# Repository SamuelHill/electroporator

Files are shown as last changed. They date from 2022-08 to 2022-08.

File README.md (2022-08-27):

# Electroporator PCB

Various PCB designs for a simple, versatile, and inexpensive electroporator. Inspiration and original design from [T. Bullman, et. al. 2015](https://onlinelibrary.wiley.com/doi/10.1111/dgd.12216). As stated in the paper:

> Electroporation is a useful technique to study gene function during development but its broad application is hampered due to the expensive equipment needed.

While I agree with this and the rest of the paper largely, I believe the design set forth is both cluttered and unnecessarily complicated. This is mainly due to the use of a breadboard (or PCB breadboard), and given the current capabilities and price point of manufacturing a custom PCB this seems the obvious place to start for simplification. To that end, I designed a simple PCB that also contains much of the needed information for construction and operation on the silkscreen. After successfully implementing and using the v.0 system, I also designed and am working on implementing a handful of v.1 boards.

The layout of this project is a series of nested KiCad projects for easy navigation within KiCad. To better show the functionality of the HE721A IC's - and add this product and footprint - I created a custom part (found in the parts folder). In the gerber folder is the compiled output of the v.0 board which has been printed, tested, and used successfully. As more of the designs are tested I will add more completed gerber files. The archive folder can be ignored as it just includes some attempts at having the LED output on the electrode side of the circuit. The v0 and v1 folders contain the designs for each version and v1 contains a number of modifications that are discussed later in this readme.

## Breadboard layout

To make sure I had the circuit correct and that my parts were compatible I did a test on a breadboard just as the paper laid out.

Breadboard build:

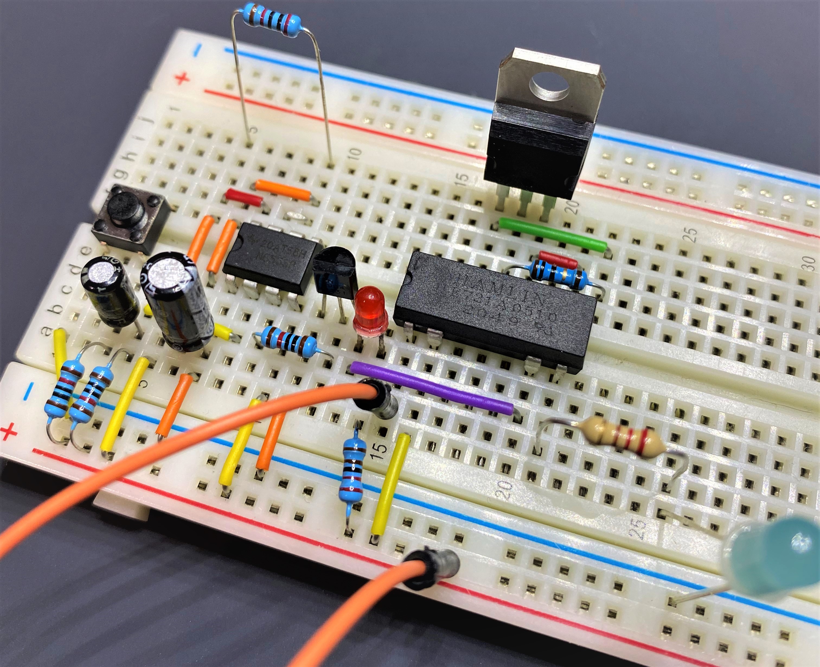
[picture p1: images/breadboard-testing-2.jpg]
Testing the circuit on a breadboard


Testing with oscilloscope:

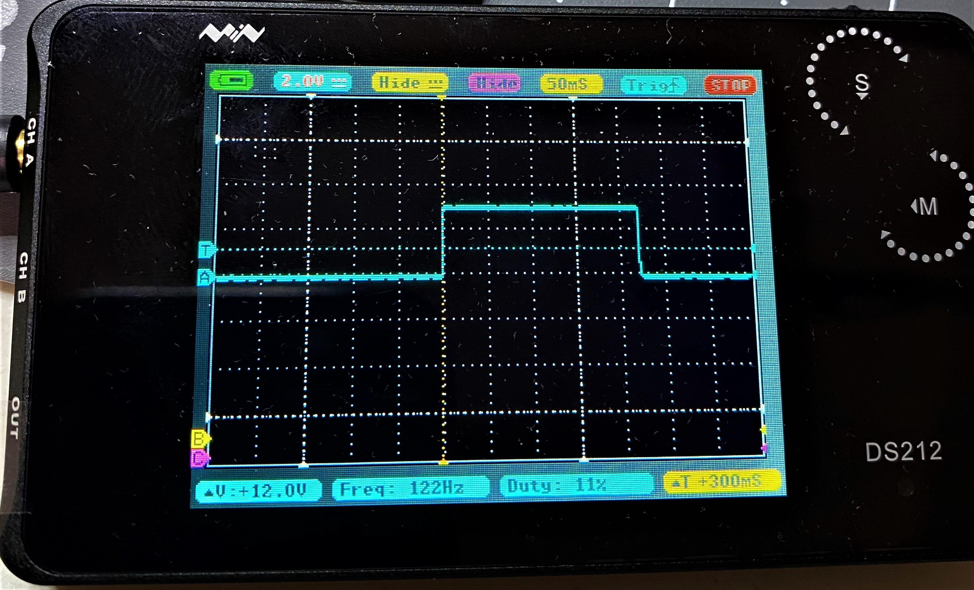
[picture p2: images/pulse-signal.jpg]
Oscilloscope output


Sizing up PCB from breadboard layout:

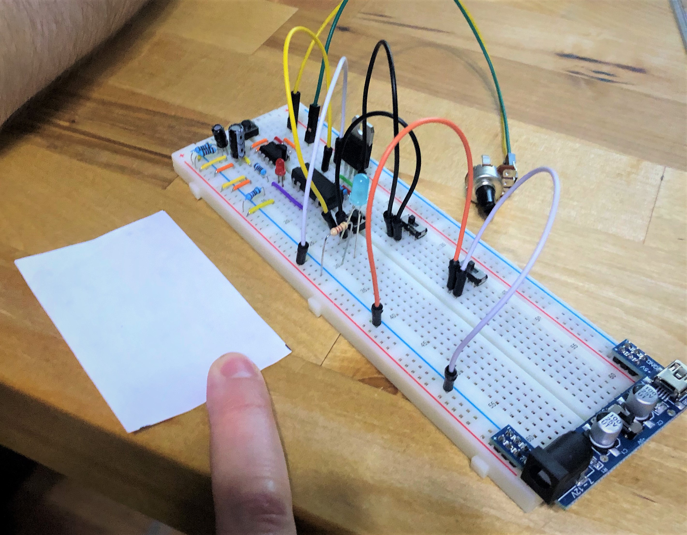
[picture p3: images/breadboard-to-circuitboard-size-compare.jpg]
Size comparison for layout of PCB


## V.0 Design

Below are 2D and 3D renders of the v.0 design:

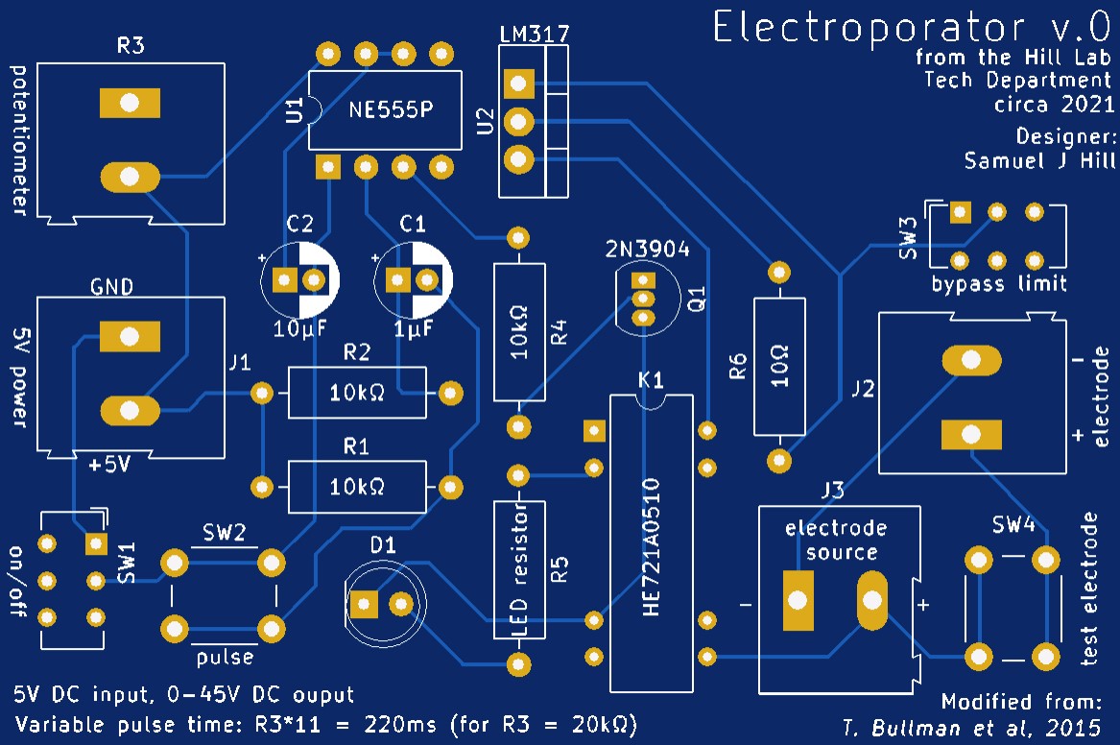
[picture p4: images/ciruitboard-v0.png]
PCB v.0 2D render


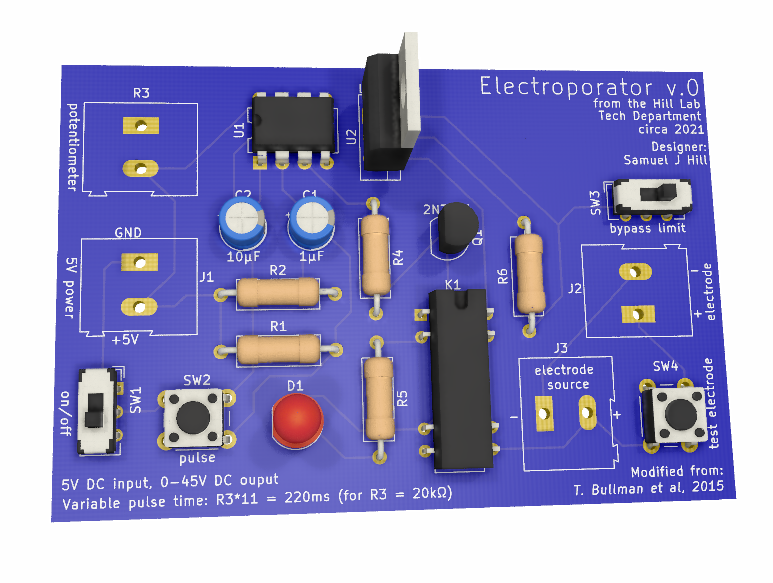
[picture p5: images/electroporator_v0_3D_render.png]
PCB v.0 3D render


This board uses the same layout as the breadboard in terms of components and connections, but - due to the nature of PCBs - doesn't require extra wiring. While the parts listed in the paper are mostly generic and easy to come by such as the resistors, capacitors, and 555 timer, the reed relay is definitely a bit more of an unusual component. While not very expensive for the kind used here, it is unlikely you have a compatible IC lying around. Also, this is another change from the paper - albeit minor - in that the PCB is only designed for reed relays and not miniature latching relays. In addition to using reed relays, I am expecting a relay with diode protection. The relays I used for my testing and builds were [HE721A0510's](https://www.mouser.com/ProductDetail/Littelfuse/HE721A0510?qs=X8LBAgEWIKIfZjBxMXqqBA%3D%3D).

## V.1 Designs *(ordered components on wait lists - _IN PROGRESS & UNTESTED_)*

The v.0 system is reasonably simple and flexible (mostly due to the standard hole spacing for various IO connection types), but there are a few improvements I have thought of while building several v.0 electroporators. To start, all v.1 PCBs do not have a switch in the electrode side of the circuit as this was confusing and seems redundant. From here, I have made a JST connector only version as JST plugs are relatively low profile, dependable, and easy to install once setup. This replaces all screw terminals, buttons and switches, LED indicators, and potentiometer connections with JST plugs - making all IO consistently implemented.

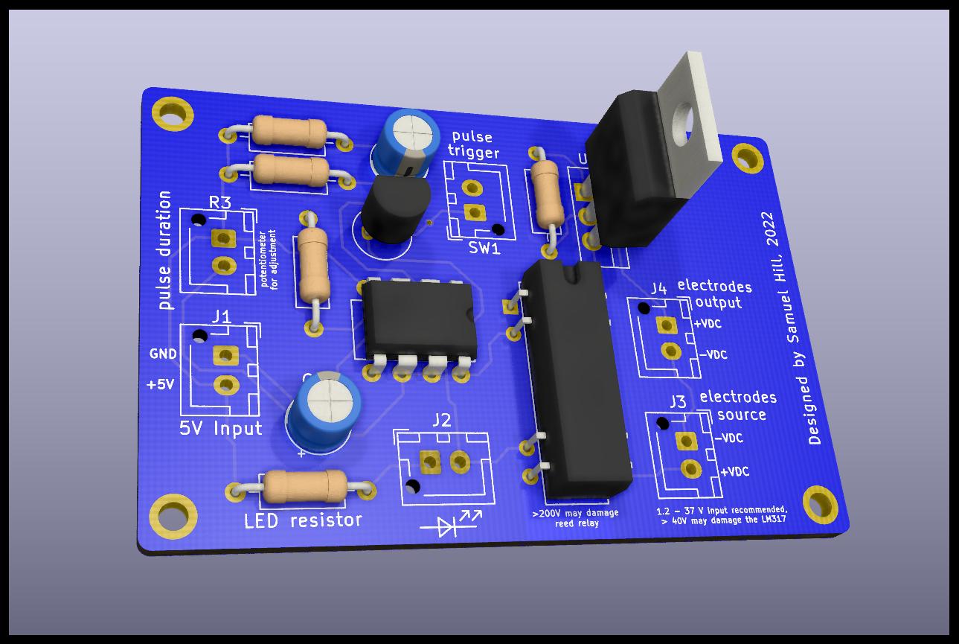
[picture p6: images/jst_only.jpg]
JST only version


The next v.1 iteration is a JST only copy with a more powerful current regulator in the form of a TL783. While previous versions were limited by the current regulator limitations, this version pushes further into the operational range for the reed relay and allows for pulse voltages from 1.25 to 125V. This opens up the ~45V - 125V range for systems that may require more power. To accommodate the adjust-ability of TL783 for regulating the current (I=Vref/R), R6 was beefed up to allow for radial resistors of appropriate values or a connection to appropriately spec'd potentiometers. These are the only modifications needed as the reed relay and JST connectors can already handle these voltages.

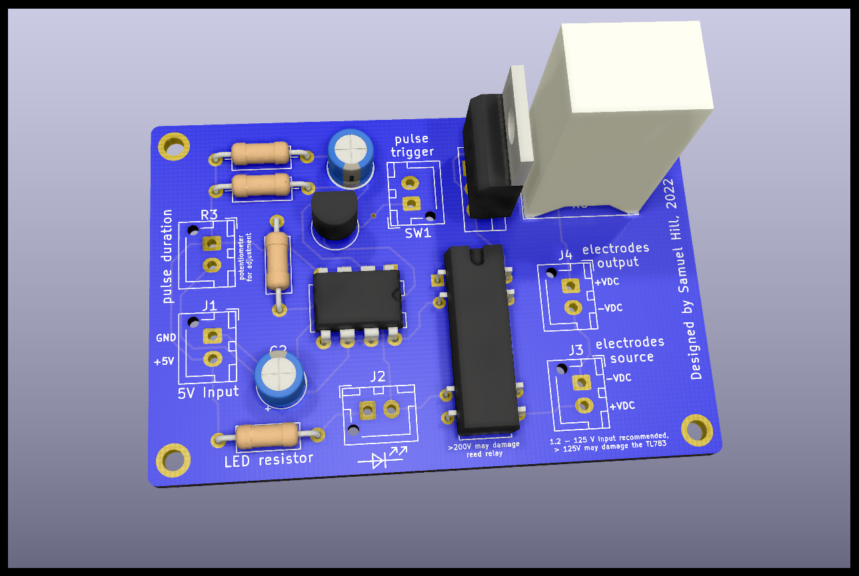
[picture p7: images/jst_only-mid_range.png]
JST only mid-range version


The JST only version could also be considered bloated if you know that your voltage is current regulated. If you were using a lab bench power supply with the current limited, the welding of the reeds in the relay should not be a concern. As such, I made a version with no current regulator for the most simple version of the circuit. This also opens up the full range of up to 200V for the relay so long as your power supply can handle those outputs limited to such low current values.

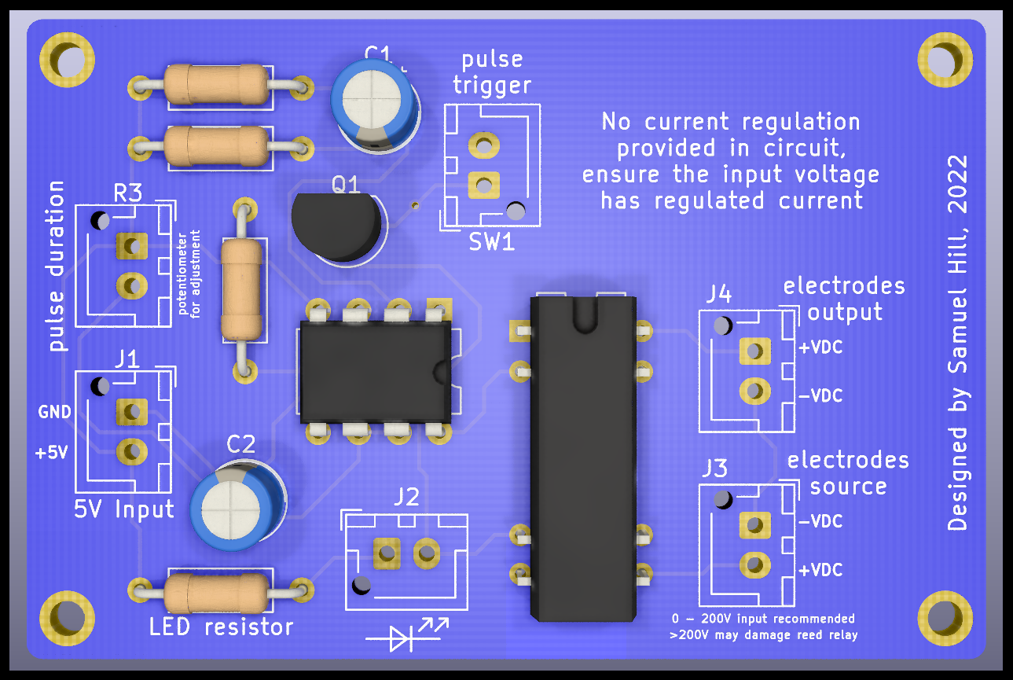
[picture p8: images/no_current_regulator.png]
JST no current regulator


Lastly, in the interest of pushing the capabilities of this design, I created a kilo-volt version. At somewhere between 5x and 10x more expensive than the HE721, and with a > 1 year lead time, the [SHV05-1A85-78D4K](https://www.mouser.com/ProductDetail/MEDER-electronic-Standex/SHV05-1A85-78D4K?qs=3BE4VKEPqliBgklxw9NVYw%3D%3D) was my choice of overpowered reed relay for this electroporator. In addition to a bigger reed relay (no current regulation like above), the JST connectors won't cut it and have been replaced with kV compatible screw terminals.

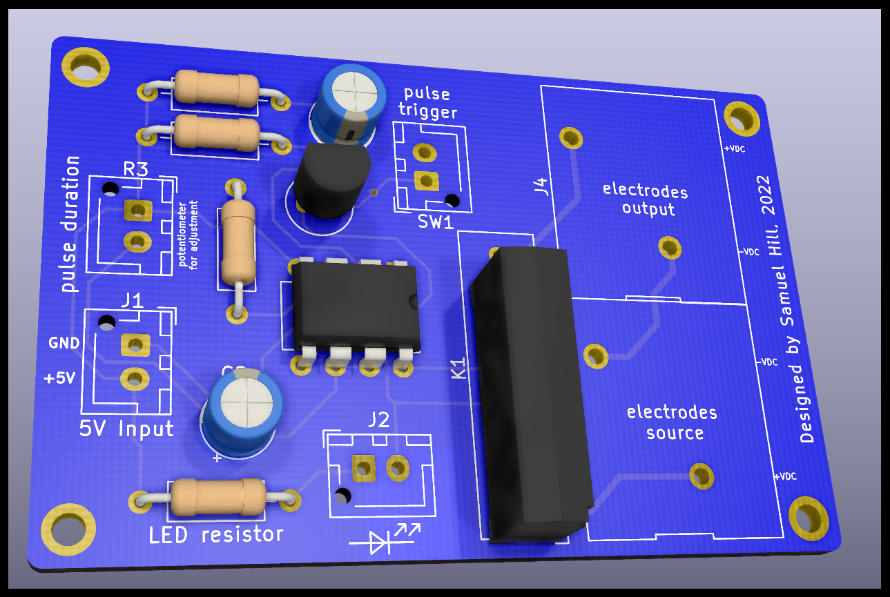
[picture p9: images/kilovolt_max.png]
Kilo-volt compatible design


## V.0 Implementations

Below are two of the implementations that went to be used in the Hill lab and have been tested on sponge cells. Imaging and further testing is ongoing.

### Large project box

#### Lid:

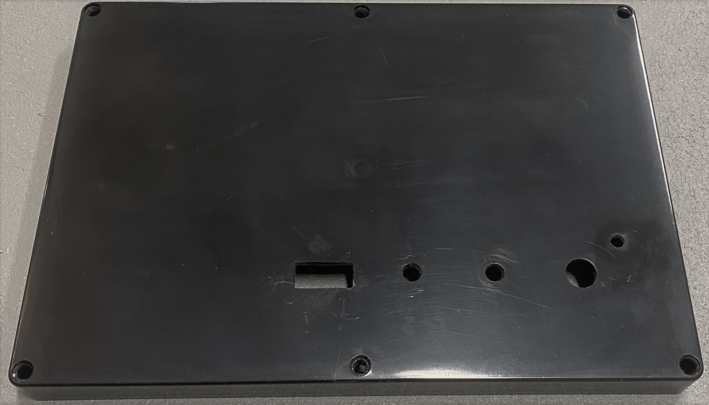
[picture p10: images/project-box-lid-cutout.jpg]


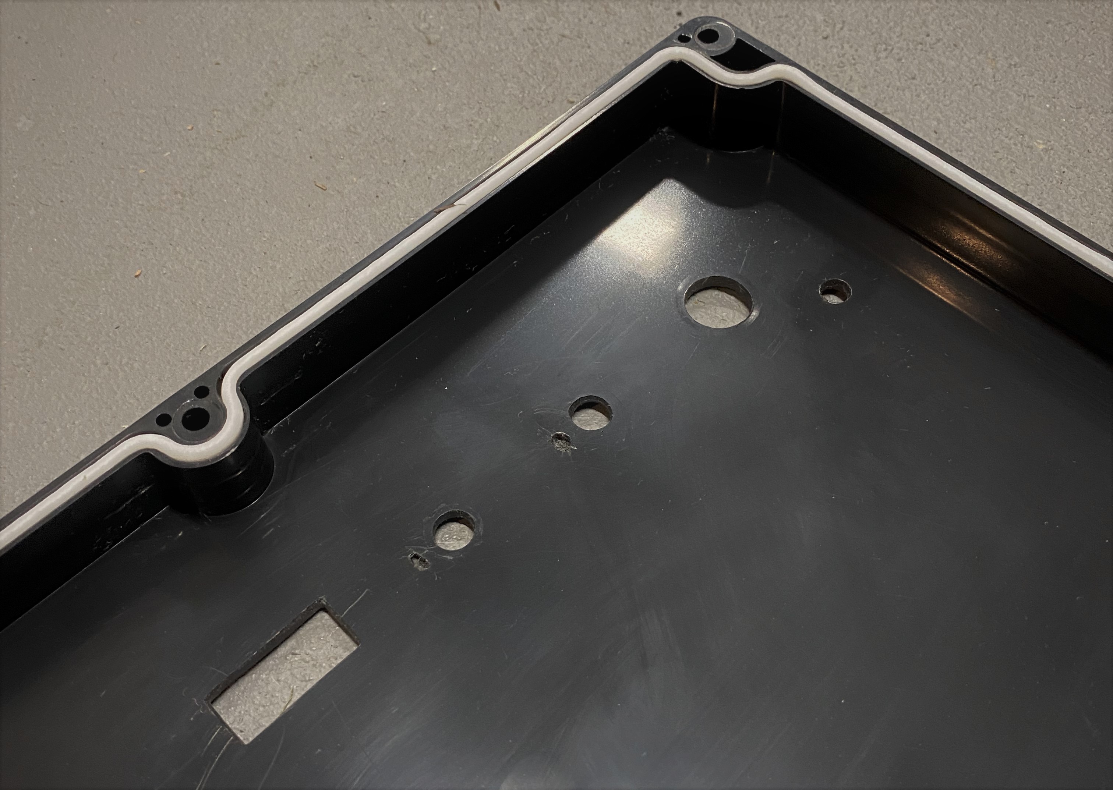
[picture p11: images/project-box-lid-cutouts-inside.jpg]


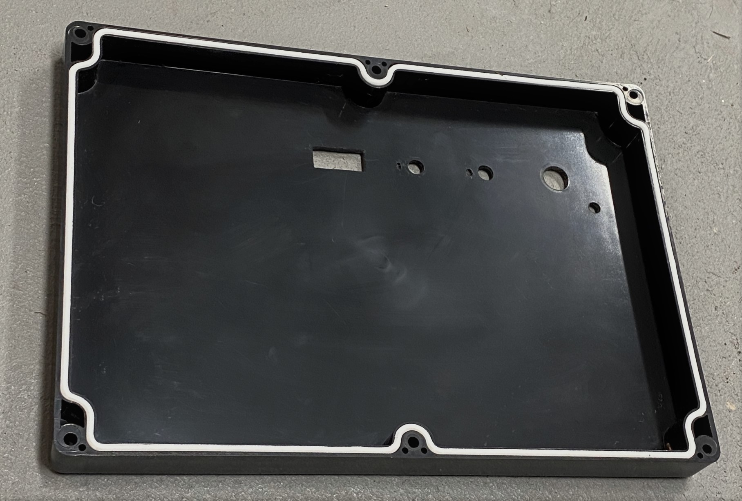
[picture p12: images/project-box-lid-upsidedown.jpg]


#### Sides:

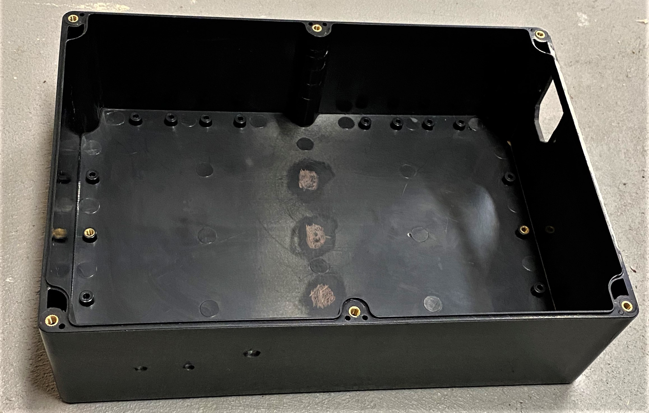
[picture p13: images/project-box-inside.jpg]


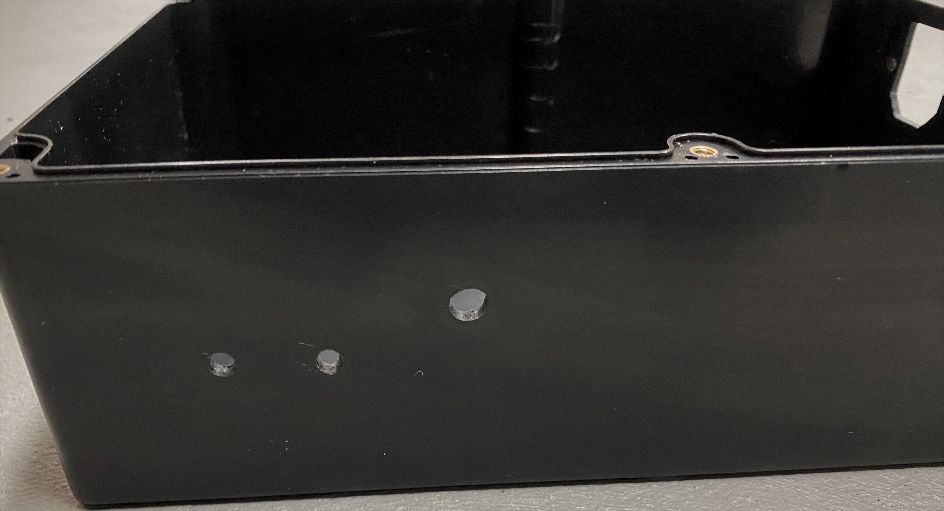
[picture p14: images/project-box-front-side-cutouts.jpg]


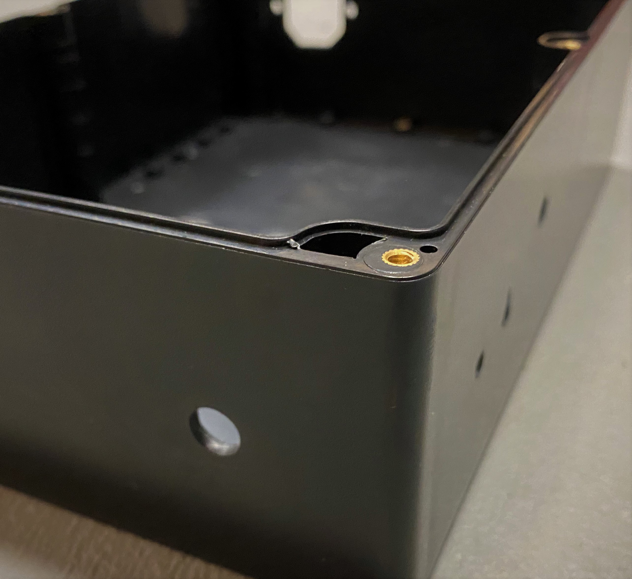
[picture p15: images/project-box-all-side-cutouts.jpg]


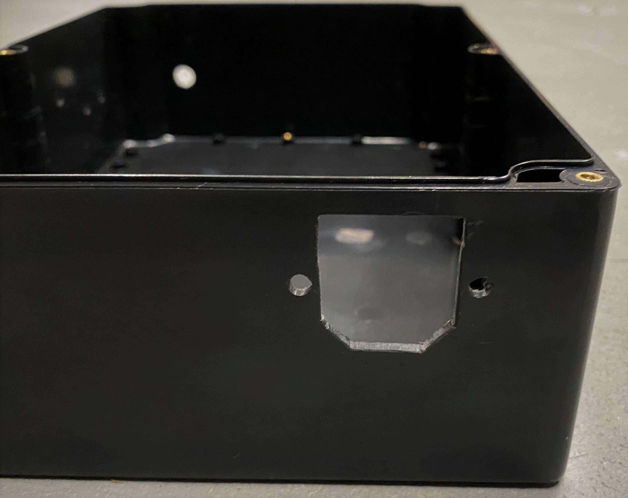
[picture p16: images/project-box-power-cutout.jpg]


#### Lid IO:

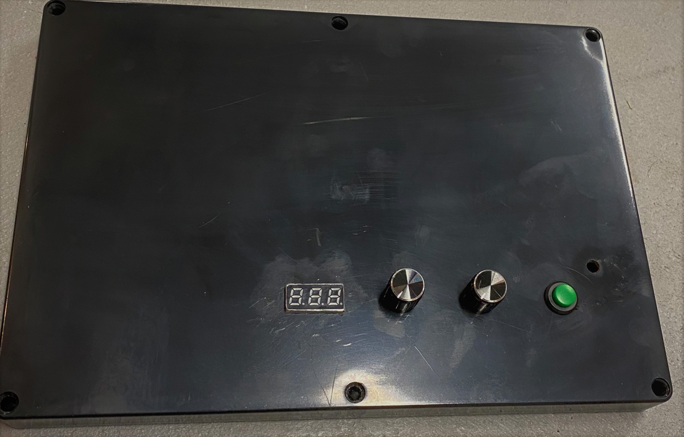
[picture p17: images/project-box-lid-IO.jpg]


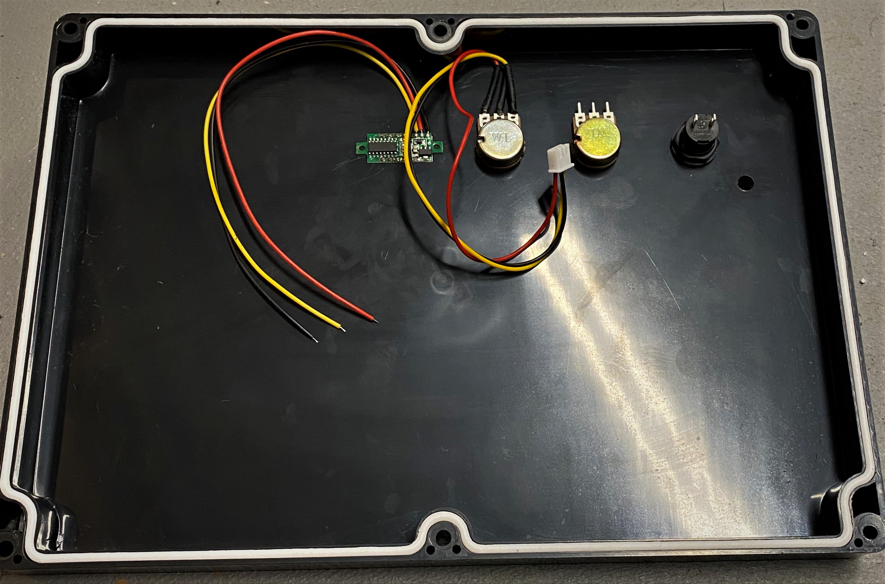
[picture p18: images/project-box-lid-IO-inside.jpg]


#### Sides IO:

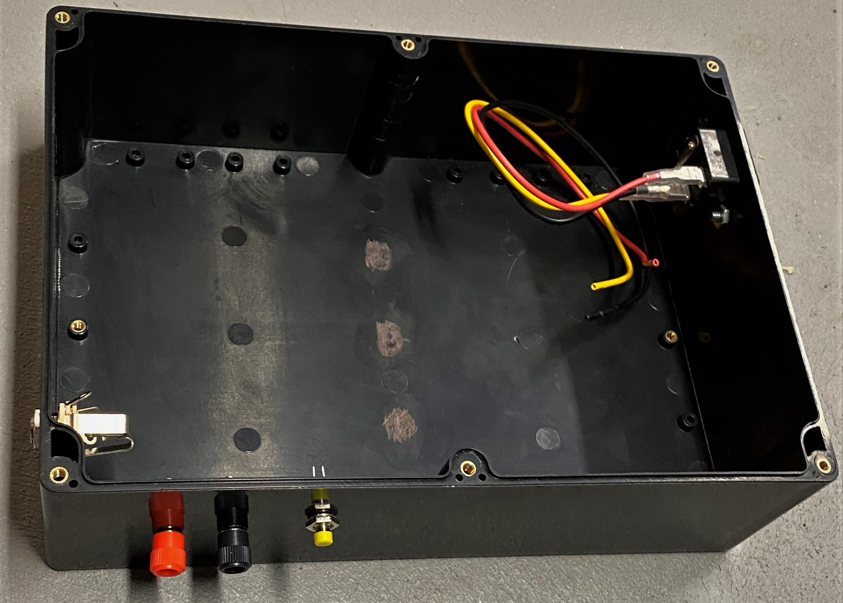
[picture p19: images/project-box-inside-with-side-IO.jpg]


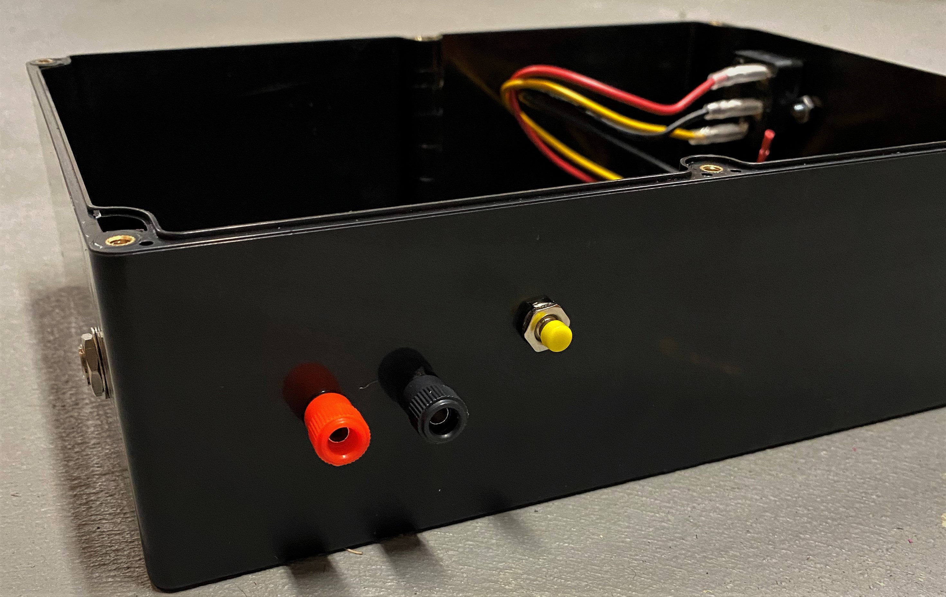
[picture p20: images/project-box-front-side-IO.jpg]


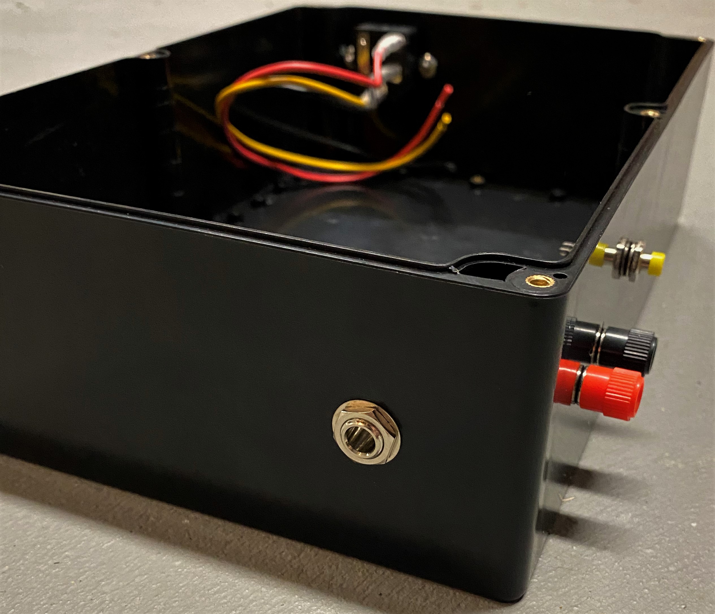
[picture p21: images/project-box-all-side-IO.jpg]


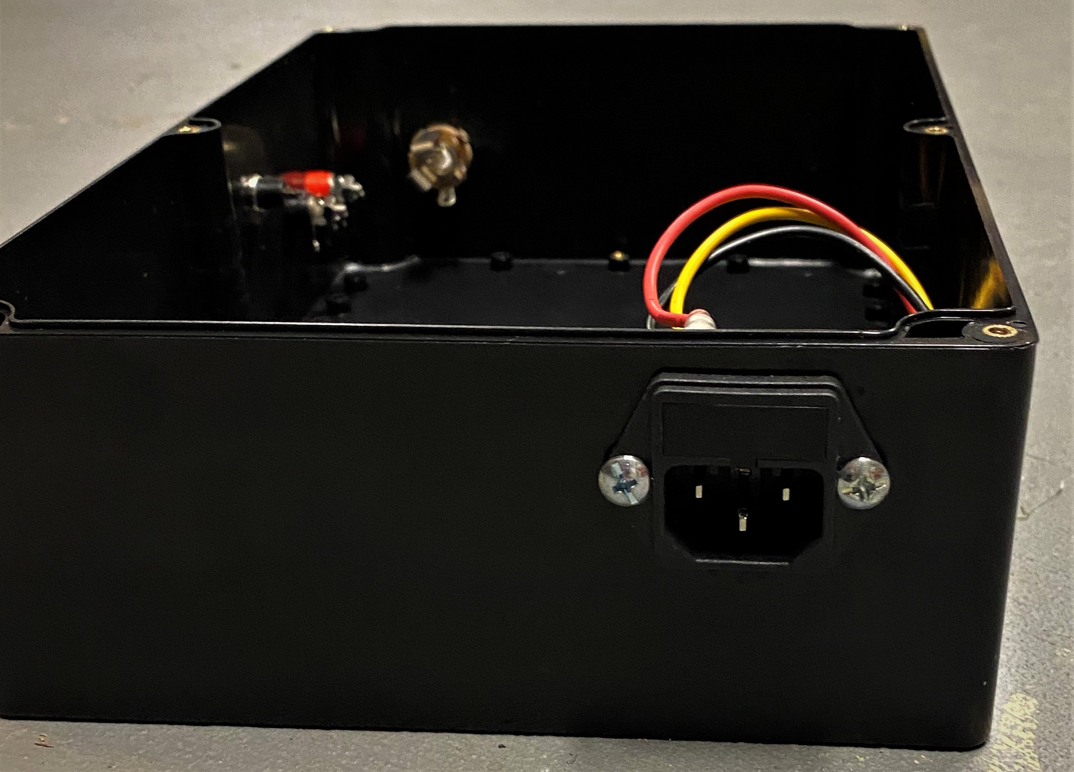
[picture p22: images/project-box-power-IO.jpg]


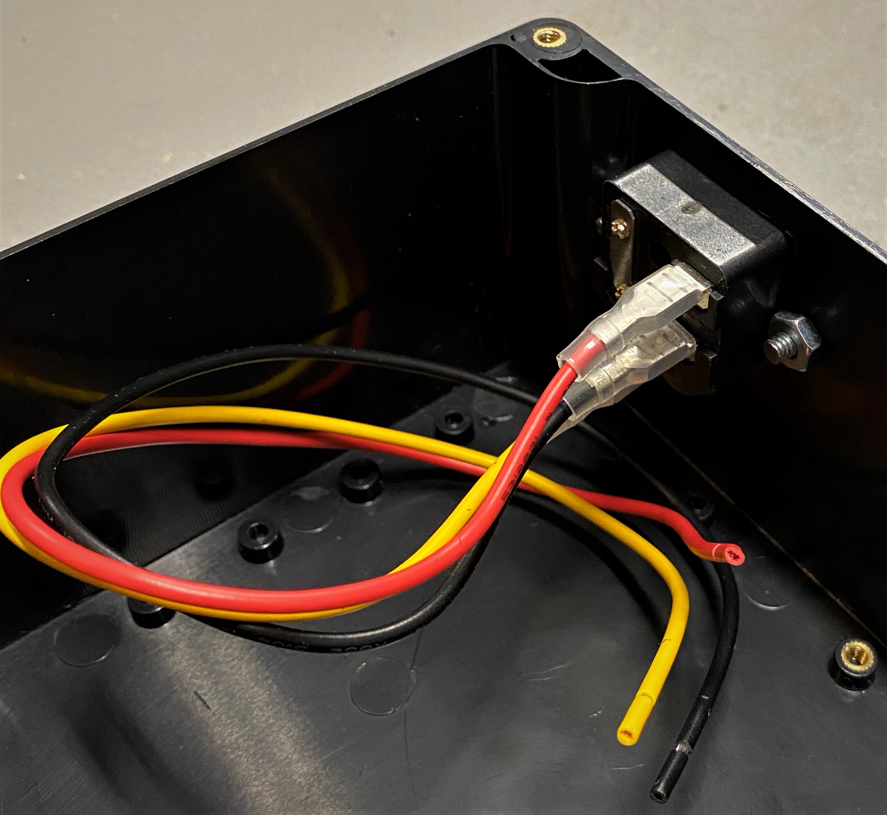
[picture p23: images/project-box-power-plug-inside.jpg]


#### IO Layout:

This is also the look of the final system (sans LED). The pulse trigger is a tattoo gun pedal so the electrodes can be positioned and operated by the users hands while the trigger can be done with your feet.

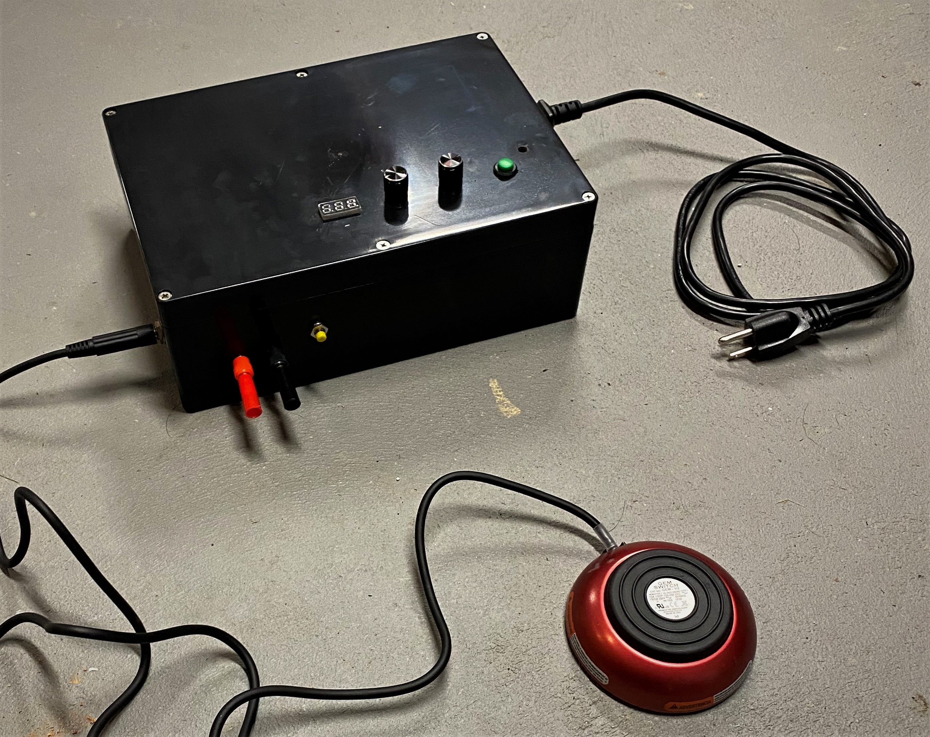
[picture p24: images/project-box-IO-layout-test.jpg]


#### Power supply:

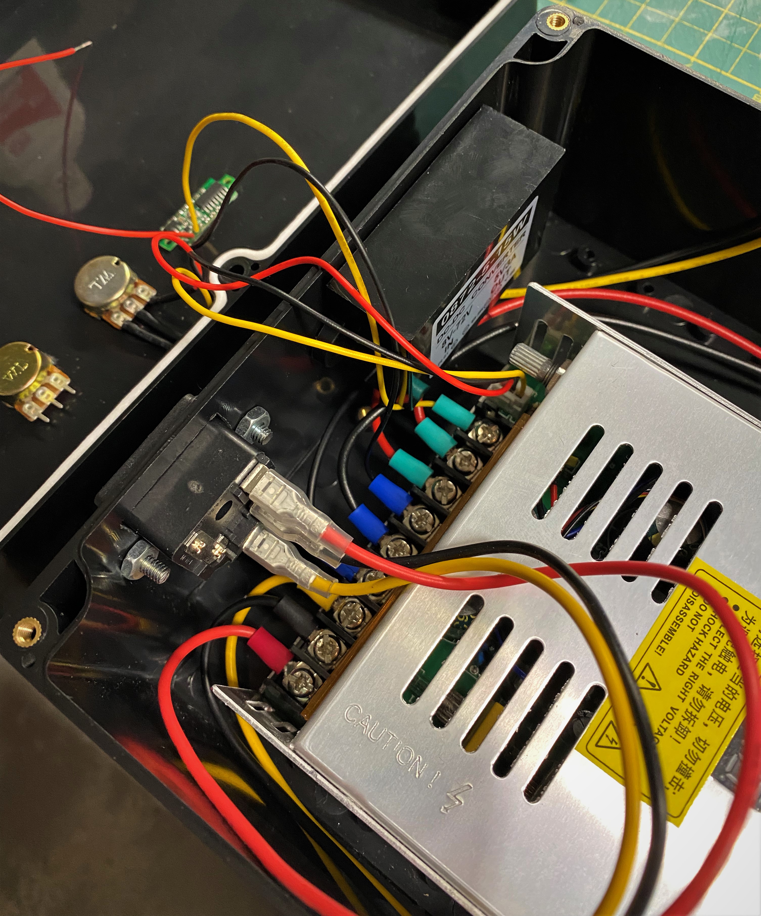
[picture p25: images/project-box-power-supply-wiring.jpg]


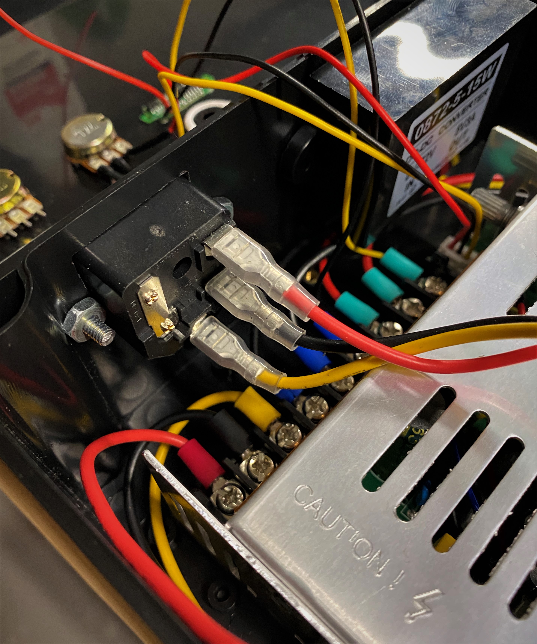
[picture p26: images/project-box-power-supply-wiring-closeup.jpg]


Yellow & black for 5V, red and black for variable power output...

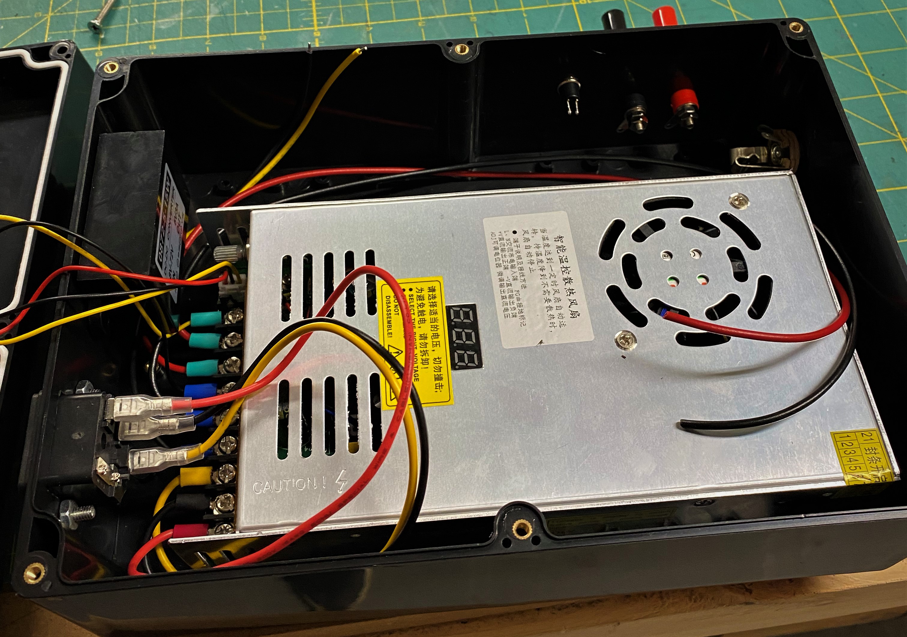
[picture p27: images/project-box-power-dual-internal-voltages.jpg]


#### Power IO:

Includes the LED for indicating when the pulse occurs...

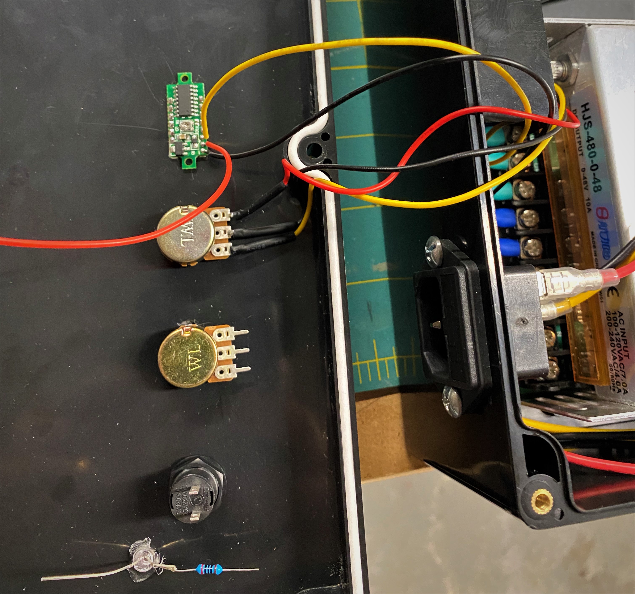
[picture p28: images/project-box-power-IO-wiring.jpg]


IO with wires attached and organized...

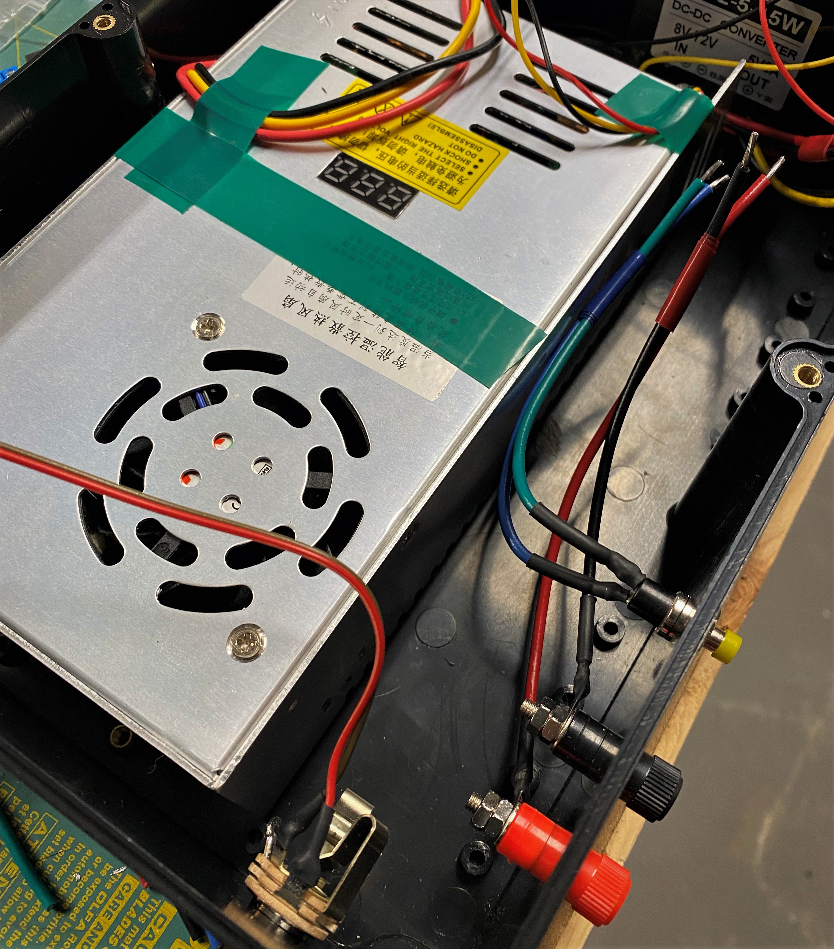
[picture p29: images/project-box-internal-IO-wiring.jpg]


Power IO removed from lid for next step...

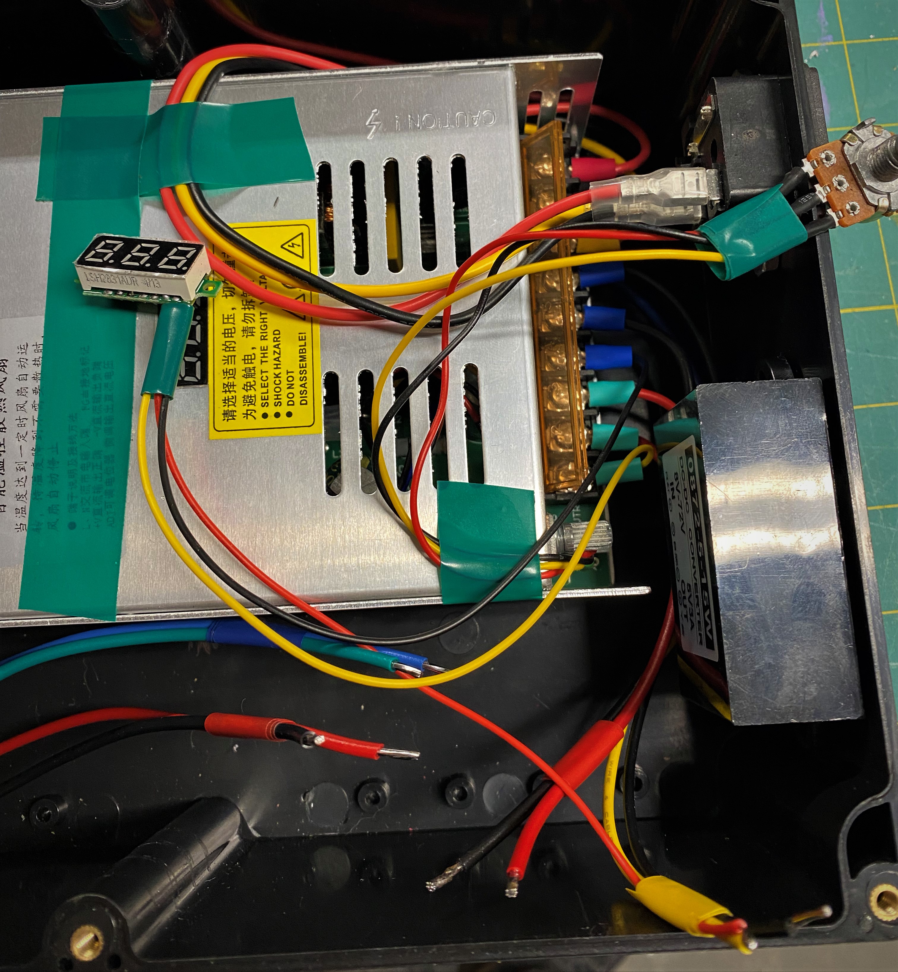
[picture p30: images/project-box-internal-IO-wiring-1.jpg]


#### PCB:

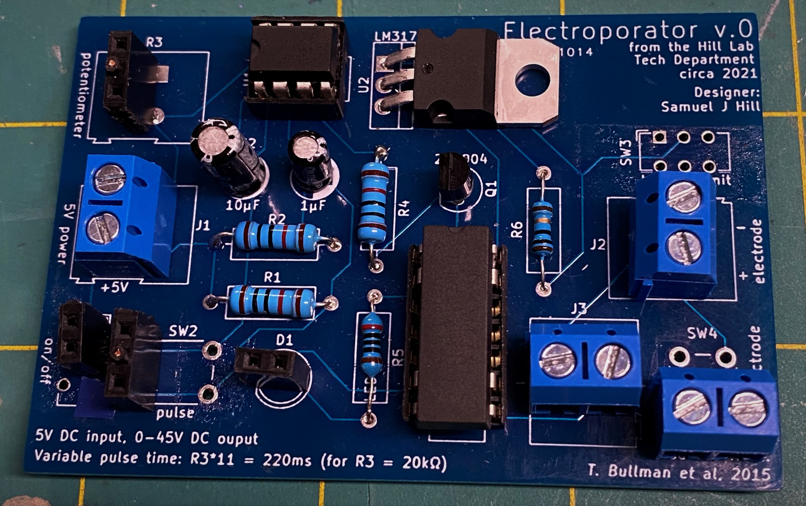
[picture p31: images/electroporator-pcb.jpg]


Power (5V and electrode variable), electrodes, and the electrode test button wiring...

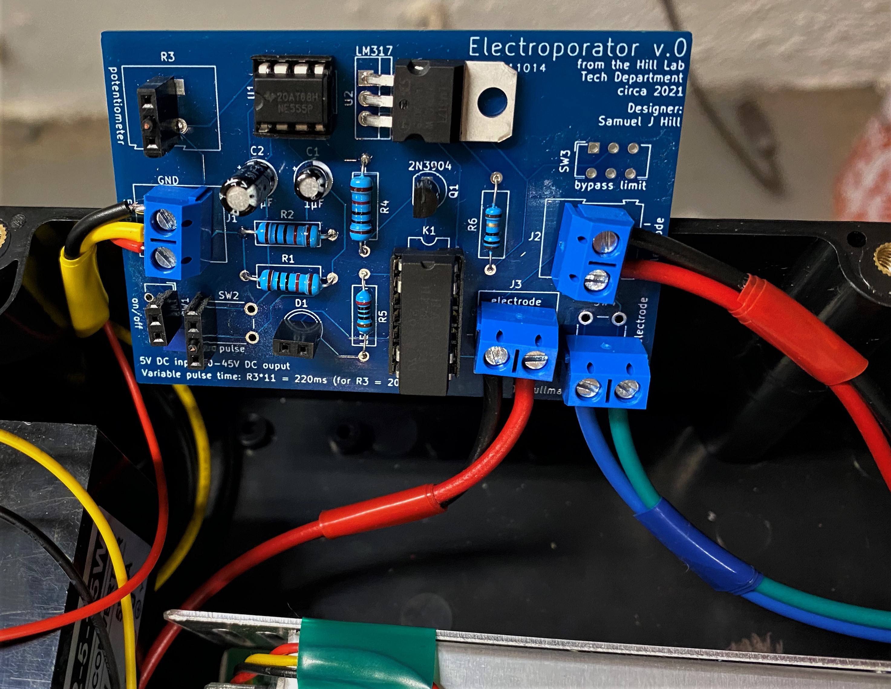
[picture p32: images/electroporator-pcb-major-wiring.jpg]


Power switch, pulse duration potentiometer, and pulse LED indicator control wiring...

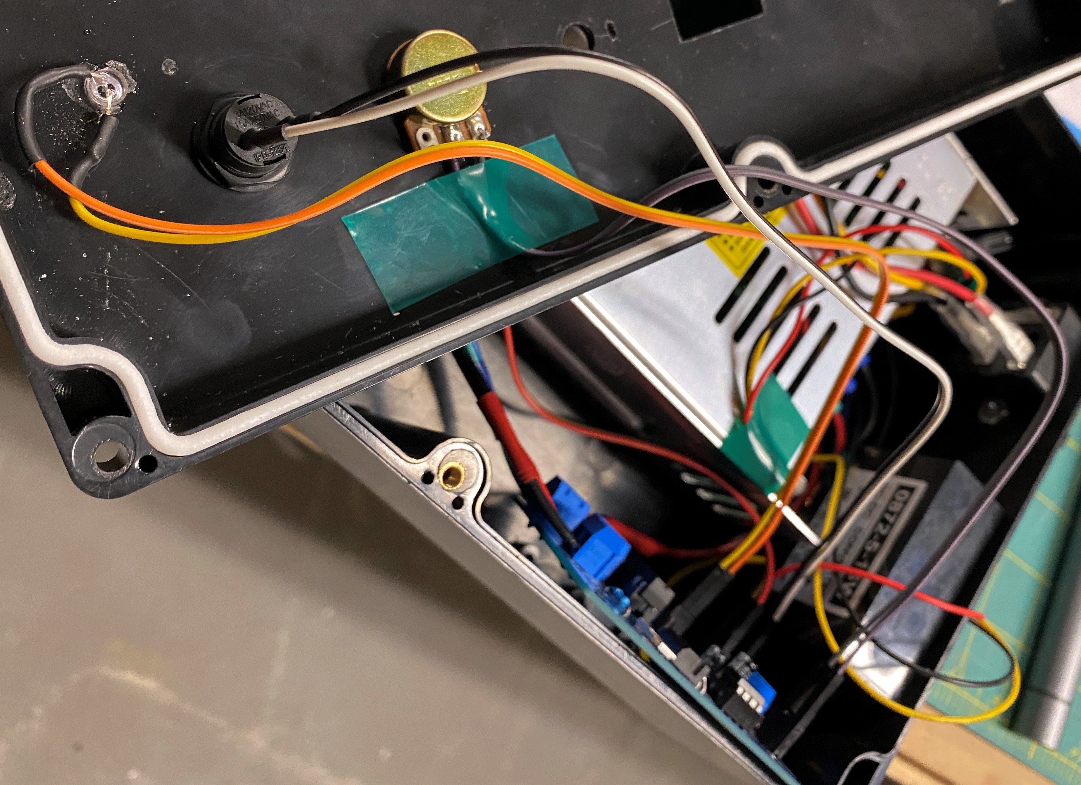
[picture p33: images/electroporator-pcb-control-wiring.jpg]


All PCB connections in place in box...

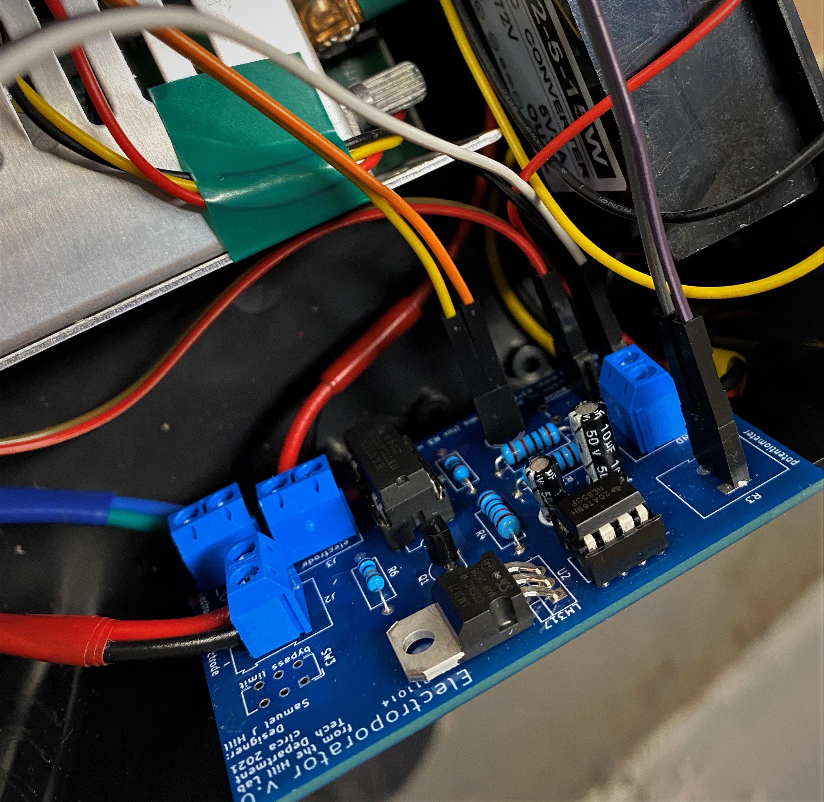
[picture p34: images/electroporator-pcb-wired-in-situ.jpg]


Cleaned up the lid wiring...

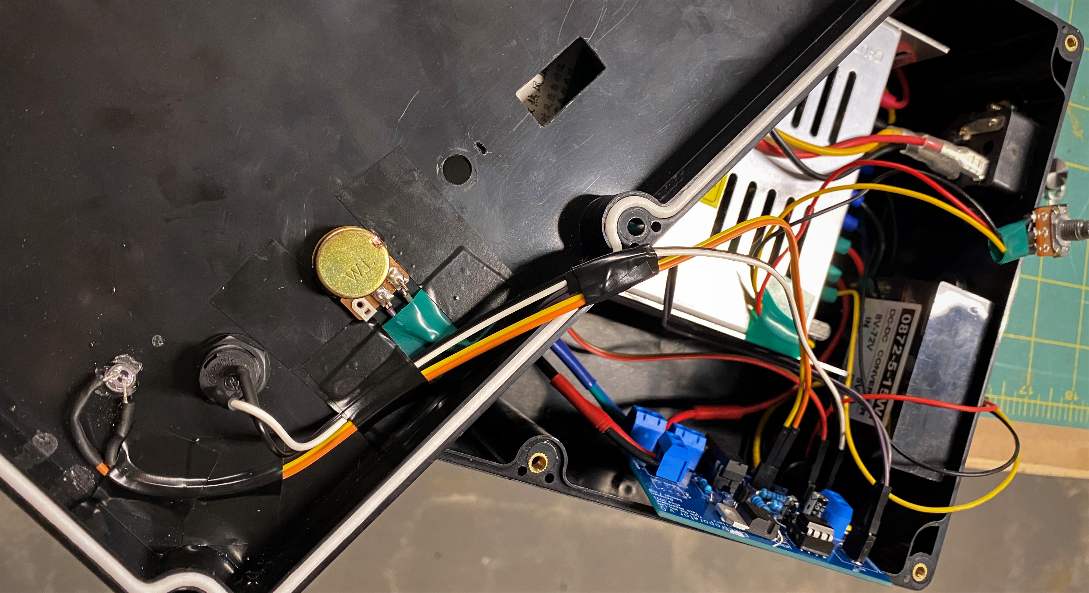
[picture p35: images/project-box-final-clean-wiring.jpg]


---

### Small project box

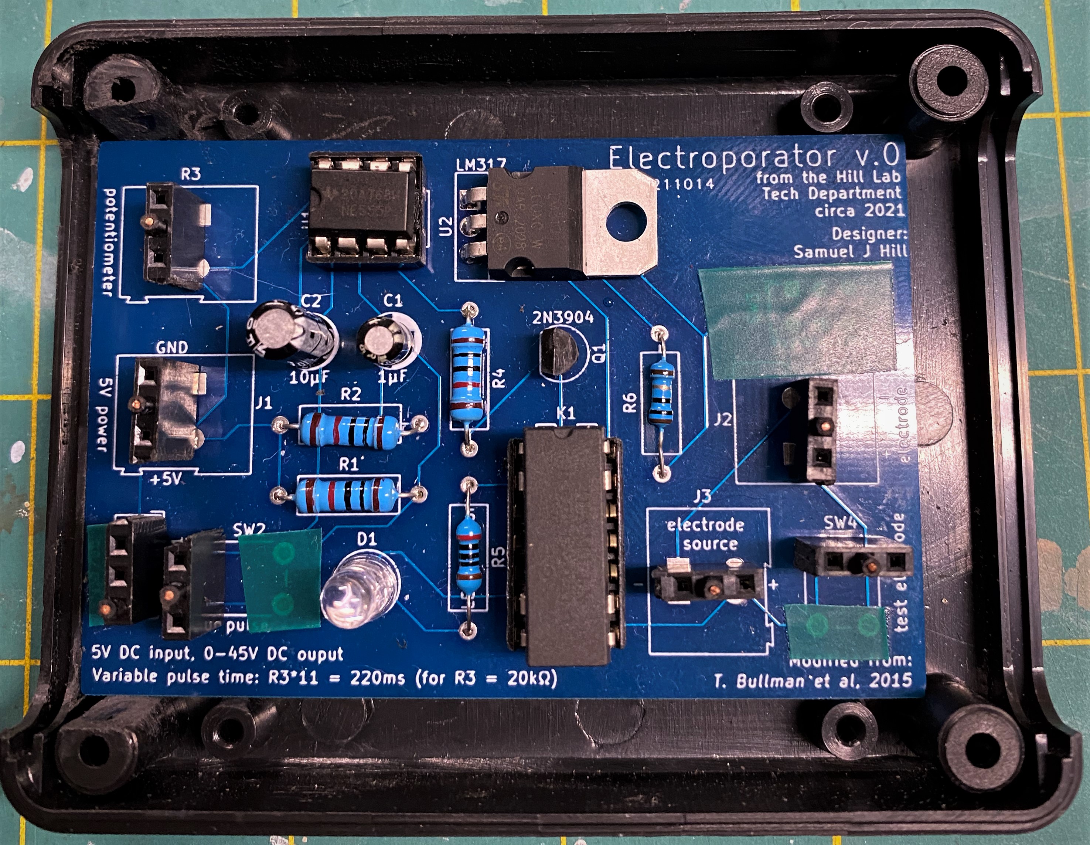
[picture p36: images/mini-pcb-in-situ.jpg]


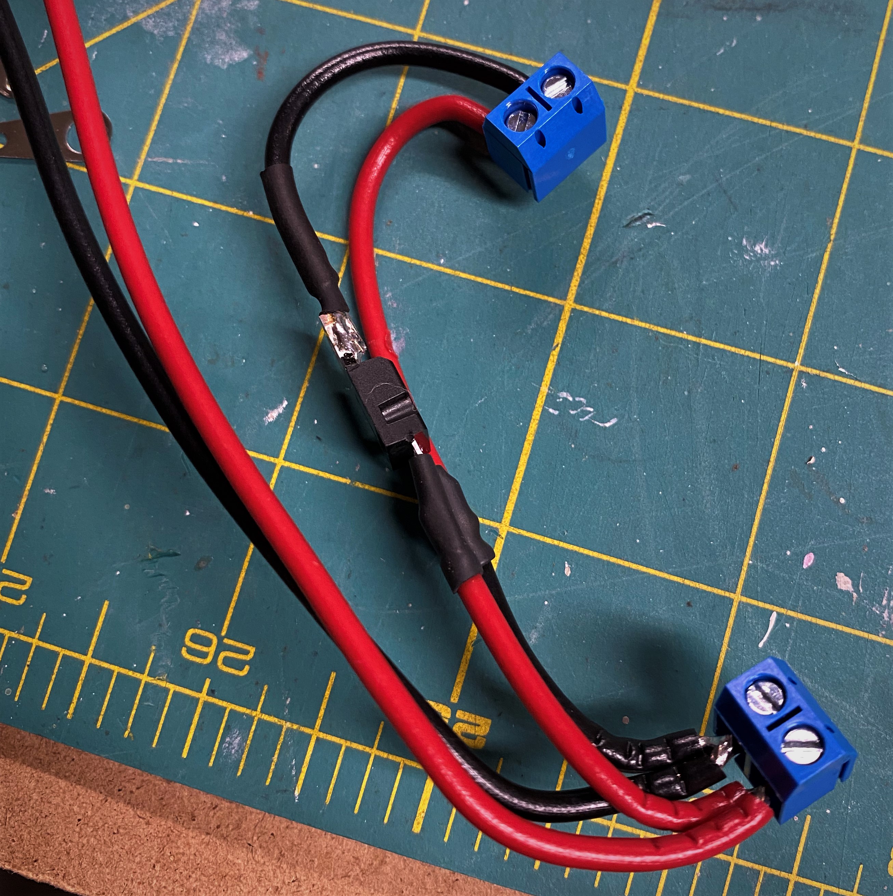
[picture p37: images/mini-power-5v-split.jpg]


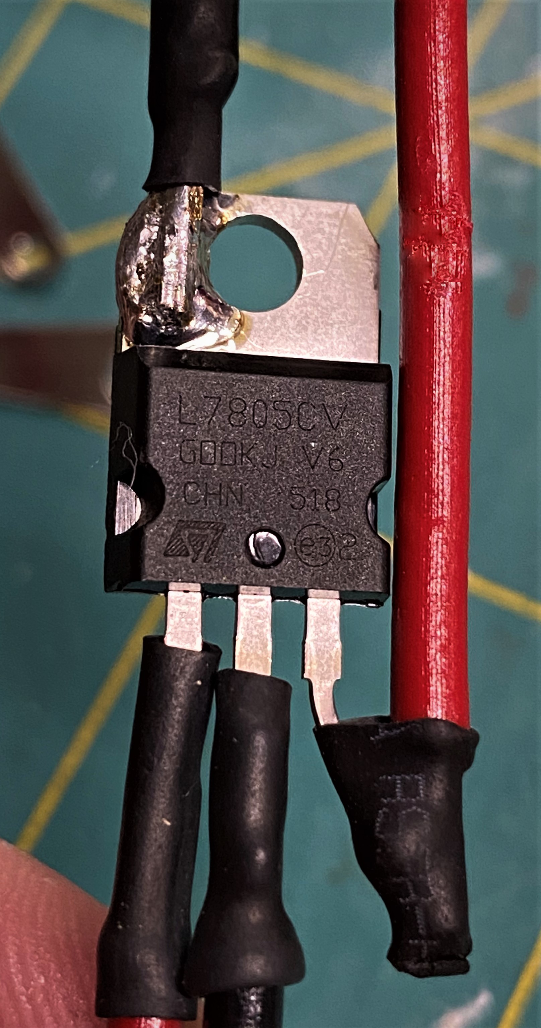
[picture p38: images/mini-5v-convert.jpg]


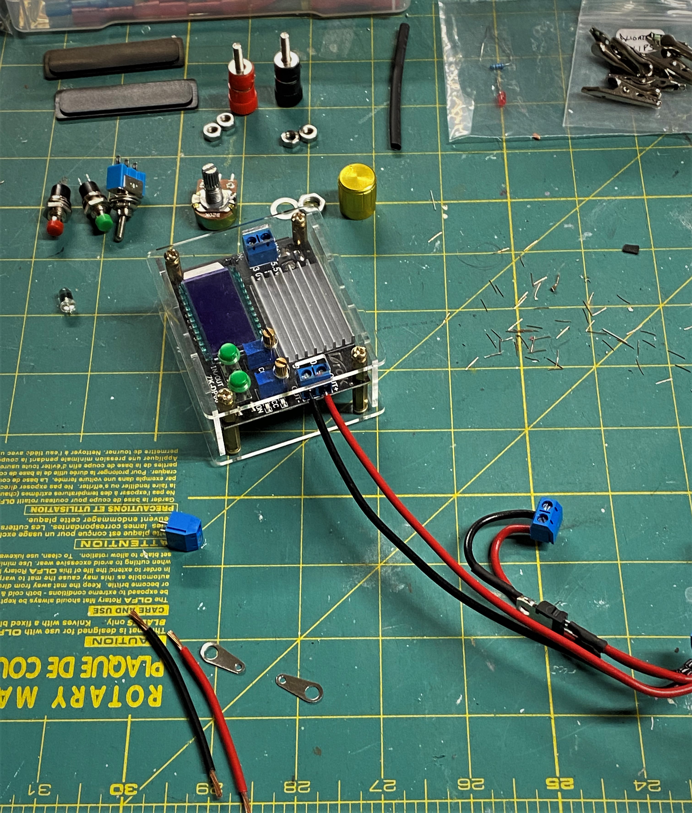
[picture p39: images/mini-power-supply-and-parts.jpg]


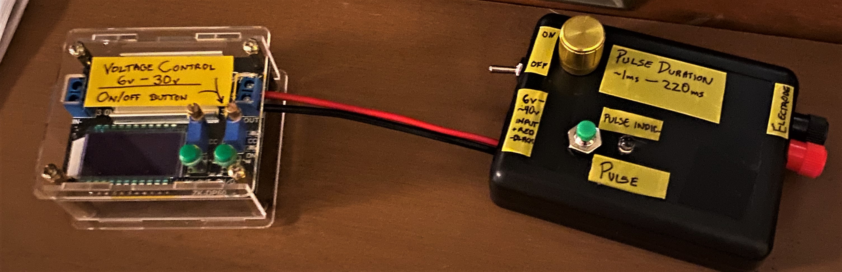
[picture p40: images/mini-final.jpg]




## Results

Using the large project box implementation in the lab with a set of adherent cell electrodes (pictured below):





Sponges (gemules adhered to some variety of 35mm glass bottom petri dish with a micro-well and cover glass) successfully electroporated with plasmids expressing GFP:





## Future work

Development of a SMT line of boards that can be both smaller and more cheaply assembled by the same sorts of PCB manufacturing facilities that allow for the cheaper custom PCBs used in this project. Many PCB production houses have assembly features wherein your board is not only printed but all available components are assembled onto the board for you. While through hole may be easier to do by hand, and is still needed for some IC's like the relay, SMT is cheaper to manufactur and assemble.

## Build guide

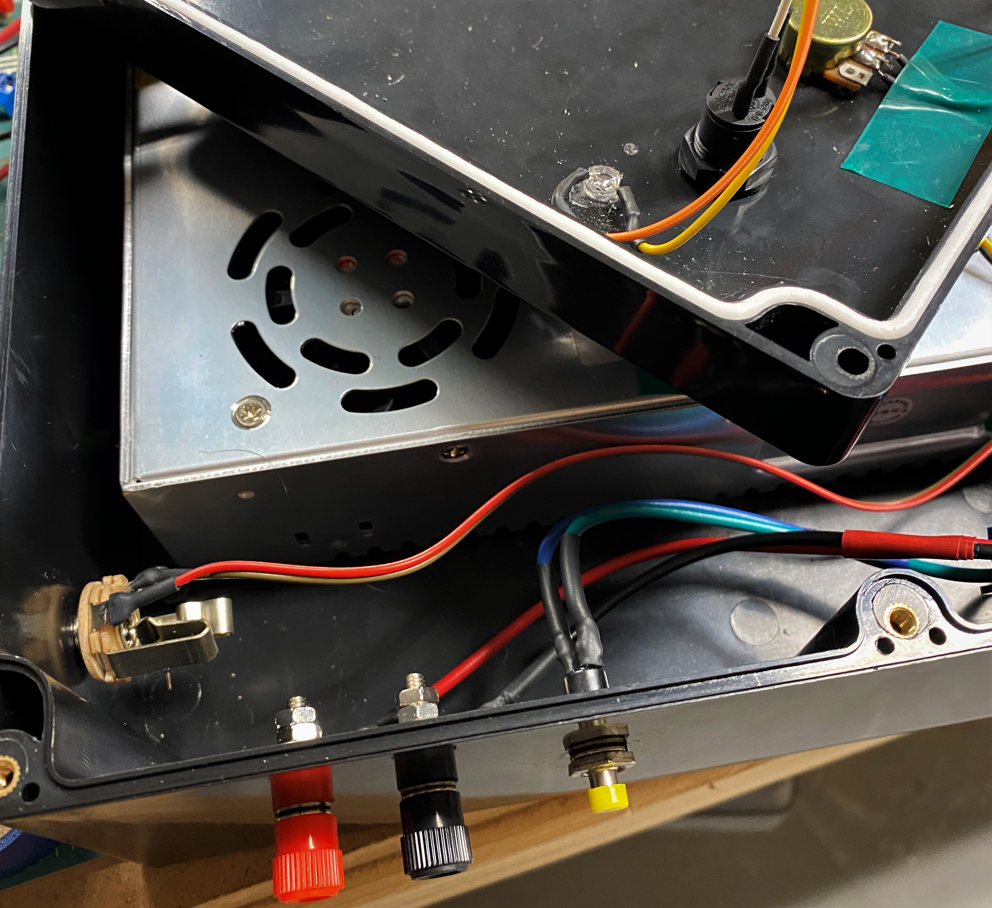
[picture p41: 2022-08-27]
images/project-box-all-IO-wiring.jpg

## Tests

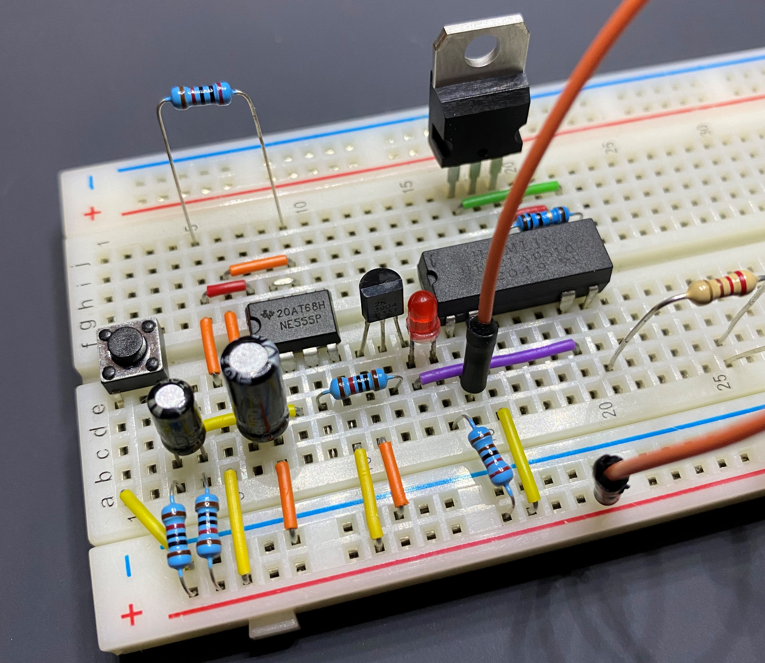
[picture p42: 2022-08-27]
images/breadboard-testing-1.jpg

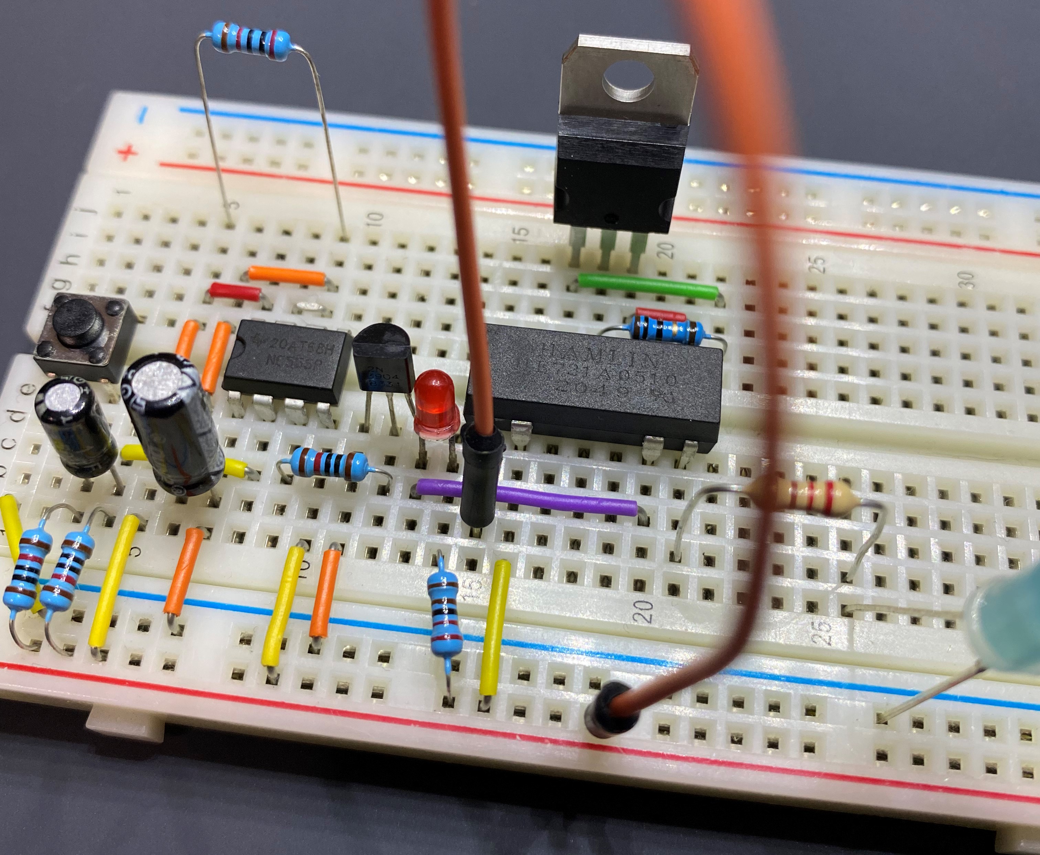
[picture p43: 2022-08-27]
images/breadboard-testing.jpg

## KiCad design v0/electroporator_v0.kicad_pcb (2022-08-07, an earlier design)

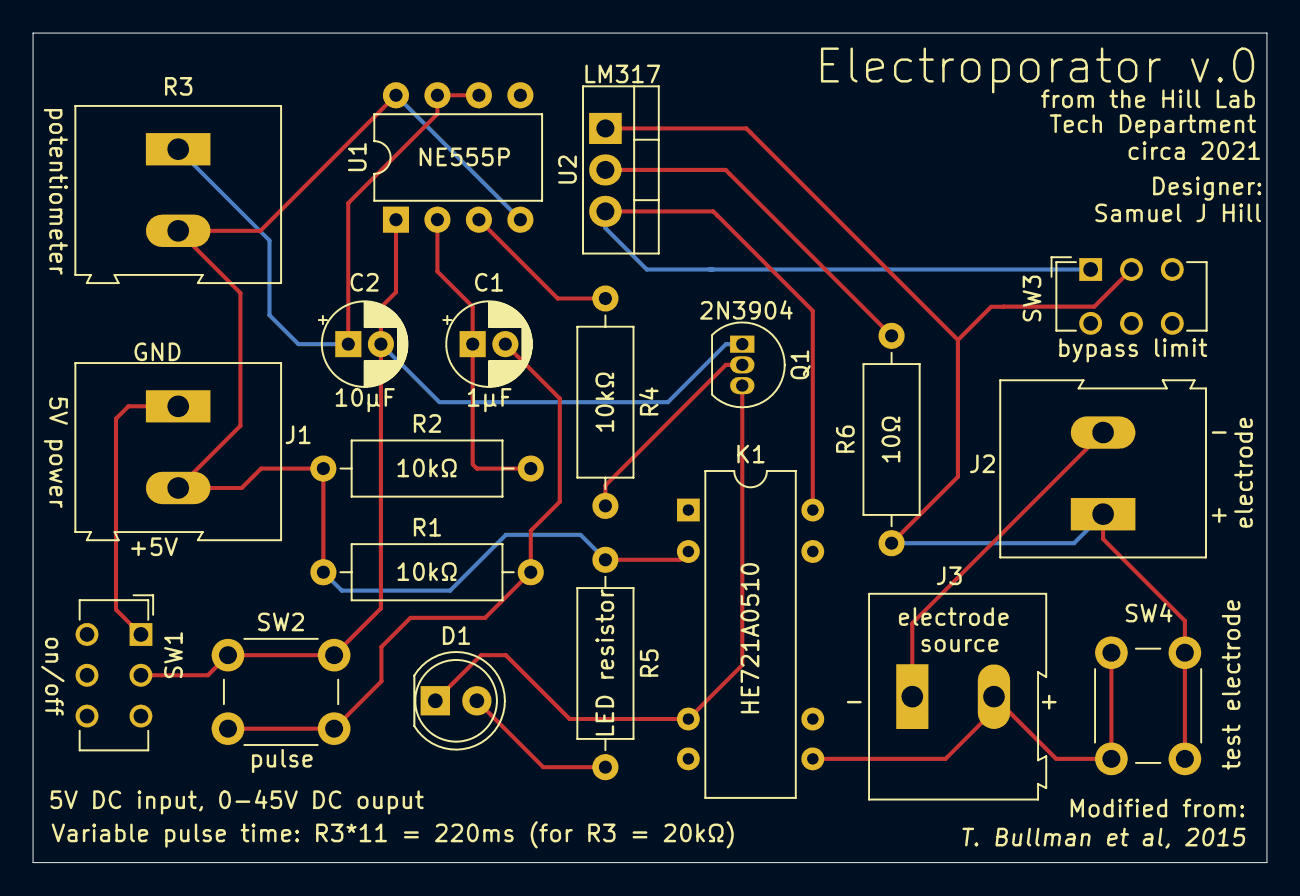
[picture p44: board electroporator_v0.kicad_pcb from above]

Board: 2 copper layers, 75.6 x 50.8 mm, 20 parts (0 on the bottom side), 15 nets.

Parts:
C1: 1µF; CP_Radial_D5.0mm_P2.00mm
C2: 10µF; CP_Radial_D5.0mm_P2.00mm
D1: LED; LED_D5.0mm
J1: 5V Input; TerminalBlock_Altech_AK300-2_P5.00mm
J2: Electrodes Out; TerminalBlock_Altech_AK300-2_P5.00mm
J3: 0-45V Input; TerminalBlock_Altech_AK300-2_P5.00mm
K1: HE721A0510; Relay_StandexMeder_DIP_LowProfile
Q1: 2N3904; TO-92_Inline
R1, R2, R4: 10kΩ; R_Axial_DIN0309_L9.0mm_D3.2mm_P12.70mm_Horizontal
R3: 20kΩ Pot; TerminalBlock_Altech_AK300-2_P5.00mm
R5: 2kΩ; R_Axial_DIN0309_L9.0mm_D3.2mm_P12.70mm_Horizontal
R6: 10Ω; R_Axial_DIN0309_L9.0mm_D3.2mm_P12.70mm_Horizontal
SW1: On/Off; SW_CuK_JS202011CQN_DPDT_Straight
SW2: Pulse; SW_PUSH_6mm
SW3: Limiter Bypass; SW_CuK_JS202011CQN_DPDT_Straight
SW4: Test electrodes; SW_PUSH_6mm
U1: NE555P; DIP-8_W7.62mm
U2: LM317; TO-220-3_Vertical

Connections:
+5V: J1.2, K1.2, R1.1, R2.1, R3.2, R5.1, U1.4, U1.8
+VDC: J3.2, K1.8, SW4.1
-VDC: J2.2, J3.1
GND: J1.1, SW1.1
unnamed: C1.1, R2.2, U1.2
unnamed: C1.2, R1.2, SW2.2
unnamed: C2.1, R3.1, U1.6, U1.7
unnamed: C2.2, Q1.1, SW1.2, SW2.1, U1.1
unnamed: D1.1, K1.6, Q1.3
unnamed: D1.2, R5.2
unnamed: J2.1, R6.2, SW3.2, SW4.2, U2.1
unnamed: K1.14, SW3.1, U2.3
unnamed: Q1.2, R4.2
unnamed: R4.1, U1.3
unnamed: R6.1, U2.2

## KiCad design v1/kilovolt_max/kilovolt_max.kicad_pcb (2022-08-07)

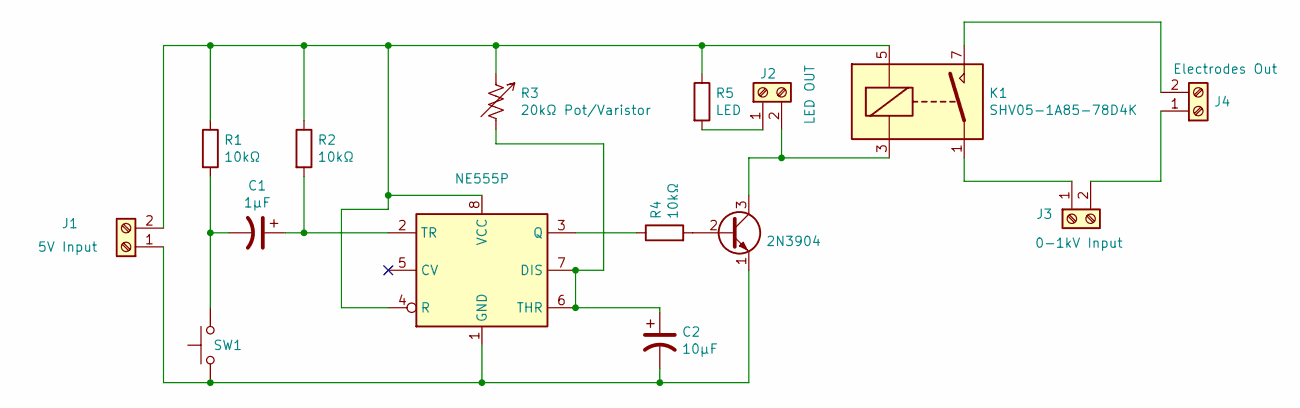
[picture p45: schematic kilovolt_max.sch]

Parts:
C1: 1µF; CP_Radial_D5.0mm_P2.00mm
C2: 10µF; CP_Radial_D5.0mm_P2.00mm
J1: 5V Input; JST_XH_B2B-XH-AM_1x02_P2.50mm_Vertical
J2: LED OUT; JST_XH_B2B-XH-AM_1x02_P2.50mm_Vertical
J3: 0-1kV Input; DIP-4_300
J4: Electrodes Out; DIP-4_300
K1: SHV05-1A85-78D4K; Relay_SPST_StandexMeder_SHV
Q1: 2N3904; TO-92_Inline
R1, R2, R4: 10kΩ; R_Axial_DIN0207_L6.3mm_D2.5mm_P10.16mm_Horizontal
R3: 20kΩ Pot/Varistor; JST_XH_B2B-XH-AM_1x02_P2.50mm_Vertical
R5: LED; R_Axial_DIN0207_L6.3mm_D2.5mm_P10.16mm_Horizontal
SW1: Pulse; JST_XH_B2B-XH-AM_1x02_P2.50mm_Vertical
U1: NE555P; DIP-8_W7.62mm

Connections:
unnamed: C1.1, R2.2, U1.2 (TR)
unnamed: C1.2, R1.2, SW1.2
unnamed: C2.1, R3.2, U1.6 (THR), U1.7 (DIS)
unnamed: C2.2, J1.1, Q1.1 (E), SW1.1, U1.1 (GND)
unnamed: J1.2, K1.5, R1.1, R2.1, R3.1, R5.1, U1.4 (R), U1.8 (VCC)
unnamed: J2.1, R5.2
unnamed: J2.2, K1.3, Q1.3 (C)
unnamed: J3.1, K1.1
unnamed: J3.2, J4.1
unnamed: J4.2, K1.7
unnamed: Q1.2 (B), R4.2
unnamed: R4.1, U1.3 (Q)

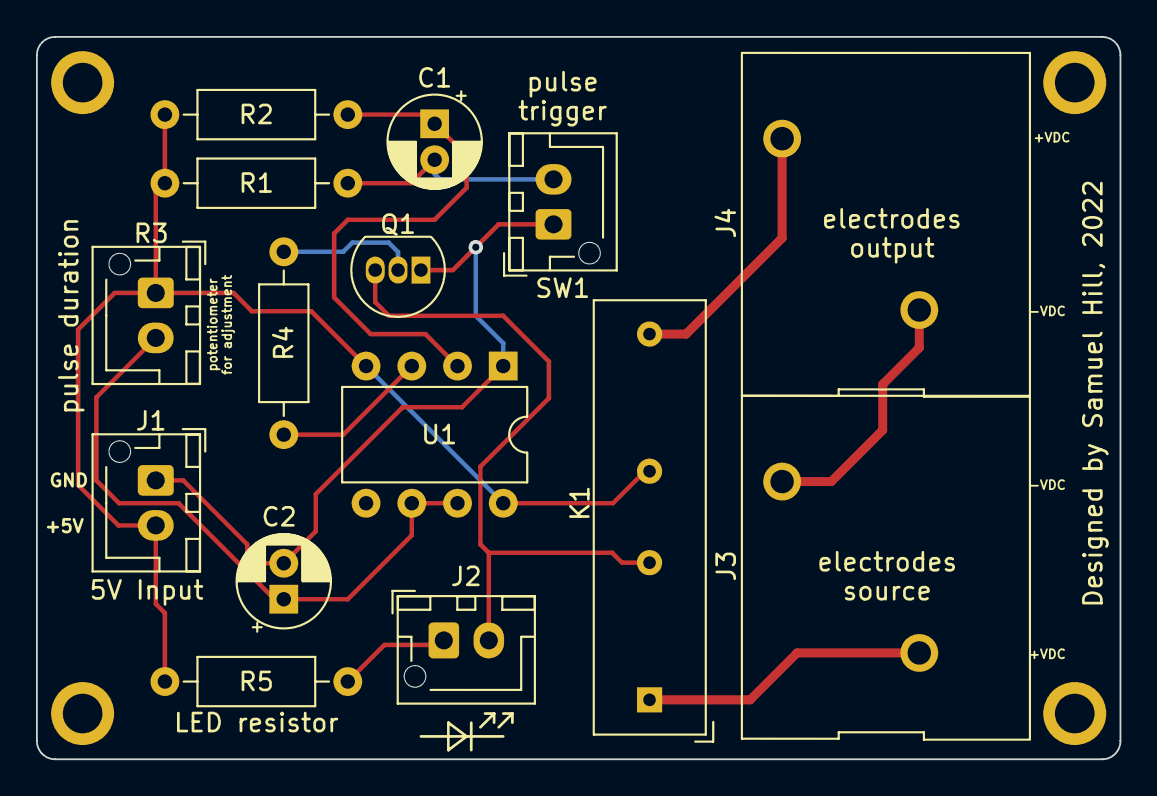
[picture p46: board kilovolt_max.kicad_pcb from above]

Board: 2 copper layers, 60.2 x 40.1 mm, 15 parts (0 on the bottom side), 12 nets.
